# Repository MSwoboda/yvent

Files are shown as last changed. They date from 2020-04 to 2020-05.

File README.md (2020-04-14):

# yVent
 
***Disclaimer:** yVent is not a medical device. yVent must not replace FDA/CE-mark ventilation support. yVent is an experimental device which should only be considered in emergency scenarios as an alternative to death due to equipment shortage.*

## Summary

yVent is a pressure-triggered, 3D printable, emergency ventilator. The device has no moving parts and consits of 2 pieces of plastic. It is designed around an aerodynamic behavior known as the Coandă effect (It is a bistable fluidic amplifier). The device produces cyclical pressure changes, which can support patient breathing, while allowing for patient actuation and eliminating the possibility of dissynchrony. The device was designed and developed as a last resort ventilator for major clinical centers in Philadelphia.

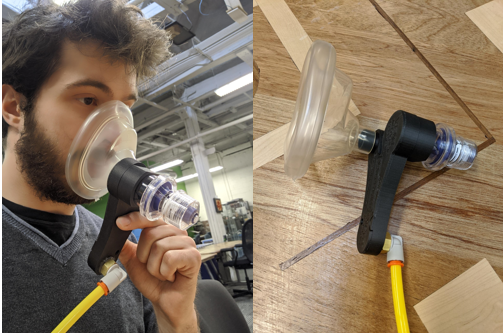
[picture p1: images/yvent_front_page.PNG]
YVENT yVent Inside


### Features
- Adjustable PIP pressure of 0-50 [cmH2O] 
- PEEP (0-20[cmH2O]) (w/ PEEP valve)
- Operating supply 20-140 [cmH2O] pressure source (air regulator or blower)  
- Can be actuated with patient breathing (no risk of asynchrony)
- Regulated inhale/exhale phase (I/E time, I/E ratio can be adjusted by modifying circuit compliance, resistance or by adding a controlled air leak)

### Risks

The device is a simple pneumatic oscillator triggered by pressure meant to sustain or support breathing. It pumps air in to a set pressure threshold, reverses flow, pumps air out to a set pressure threshold and resets. It cannot deliver a set volume of air (without an additional components), trigger alarms, display measurements, clear mucus, or perform many other critical functions of modern-day ventilators. 

### Failure Modes

yVent is reliable if the following requirements are satisfied:
1) Dimensional accuracy of the inlet and channel wedge is maintained
2) Seal of all chambers of the device is maintained
3) Air flow through the device is greater than leaks in patient circuit

yVent can fail in the following way:
- Violation of requirement 1 will change the pressure thresholds and pneumatic behavior of the circuit.
- Violation of requirement 1 may result in high frequency oscillation
- Violation of requirement 2 & 3 will result in no actuation 

## Theory of Operation

When pressure is applied to the input terminal of the yVent, the air flow stream created by the narrowing in the geometry creates a vortex (Coanda effect) which attaches the stream to the patient output channel. When the flow stream encounters resistance on the output terminal (increased pressure in patient's lungs), the first vortex collapses and the air flow stream redirects to the second output channel (again creating the Coanda effect vortex). In this fludic configuration, air flows from the patient output channel to the output terminal in addition to from the input terminal to the second terminal. This allows for exhale of gas. Once pressure in the patient's lungs reaches the threshold pressure, the second vortex collapses and restarts the cycle. Our design uses a different approach to create the Coanda vortex effect but functionally they are the same. 

## Testing and Validation

### Testing Setup
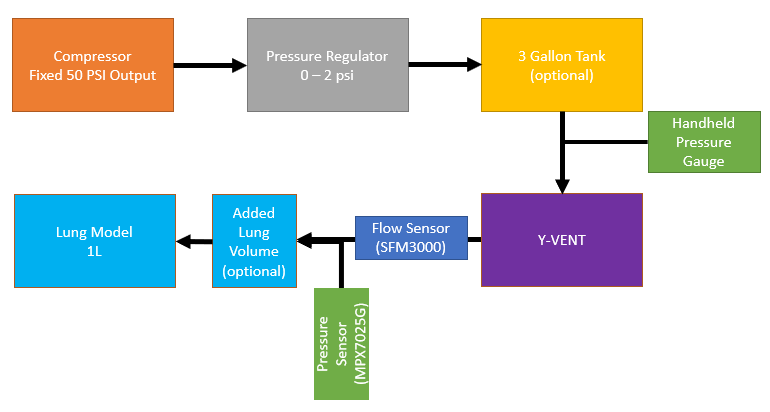
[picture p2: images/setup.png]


The testing setup aims to replicate a hospital air pressure supply of ~50 psi output connected to a 0-2 psi regulator. The pressure supply is connected to a 3 gallon tank to equalize pressure changes and flow. This is useful for testing and prototyping but not necessary for end-device as long as 2 psi regulator can provide sufficient flow to the yVent. The regulator pressure is monitored with a handheld pressure gauge.

The yVent connects to the output of the 2psi regulator and a lung simulator (MAQUET Test Lung 190 1L). The second output terminal (non-patient output) connects to a PEEP valve. The flow into the lung and pressure in the lung are monitored and recorded. The following data has been collected using this setup for two version of the yVent. Software of the measurement station can be found in the Measurement folder. Figures presented summarize the behavior of the yVent for different input pressures ranging from 40cmH2O to 120 cmH2O. If no measurement is present for a a given input pressure, it can be assumed that the device cannot work under these conditions (ex. peak inhale pressure of 20 cmH2o and 20 cmH2o PEEP causes oscillations).

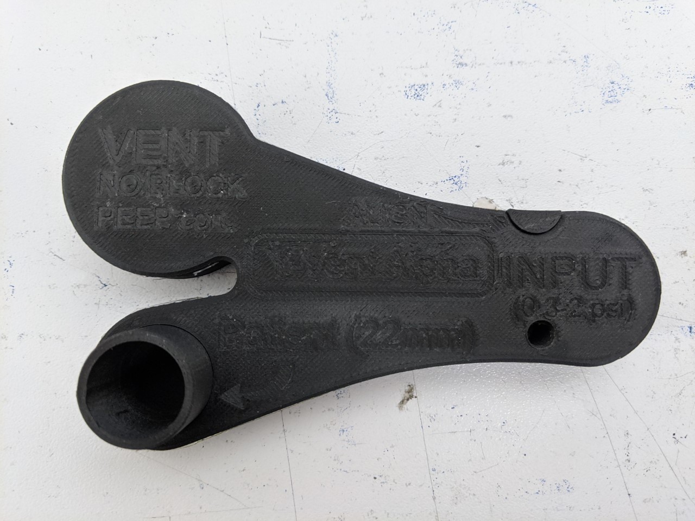
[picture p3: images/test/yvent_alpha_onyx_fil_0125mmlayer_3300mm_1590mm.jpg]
YVENT yVent Inside


### Results - Markforged 3D Printed Version [Onyx No Fiber Filament | 0.125mm layer]

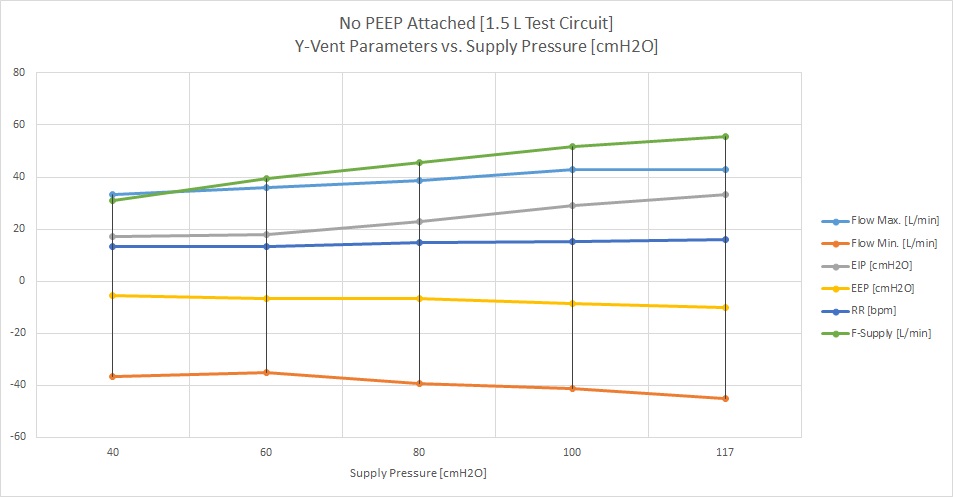
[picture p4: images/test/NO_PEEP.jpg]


Figure 1: No PEEP. 

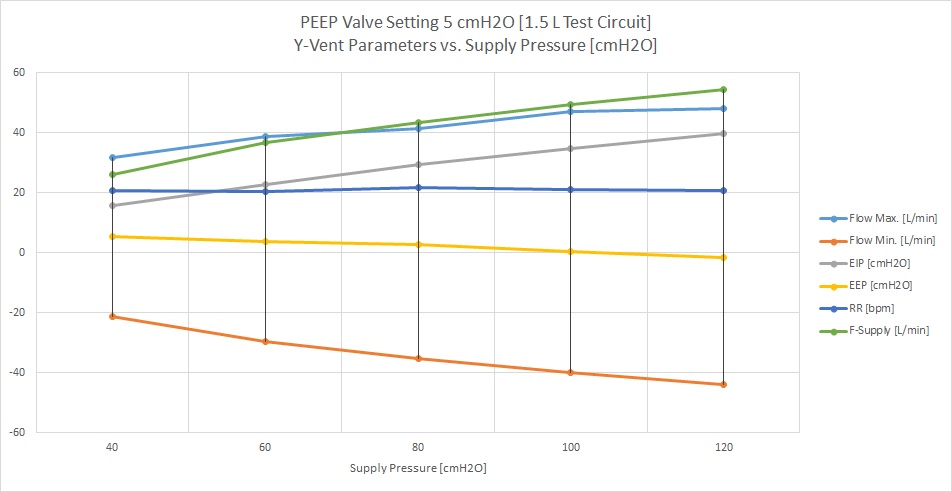
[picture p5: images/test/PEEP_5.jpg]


Figure 2: 5 cmH2O PEEP. 

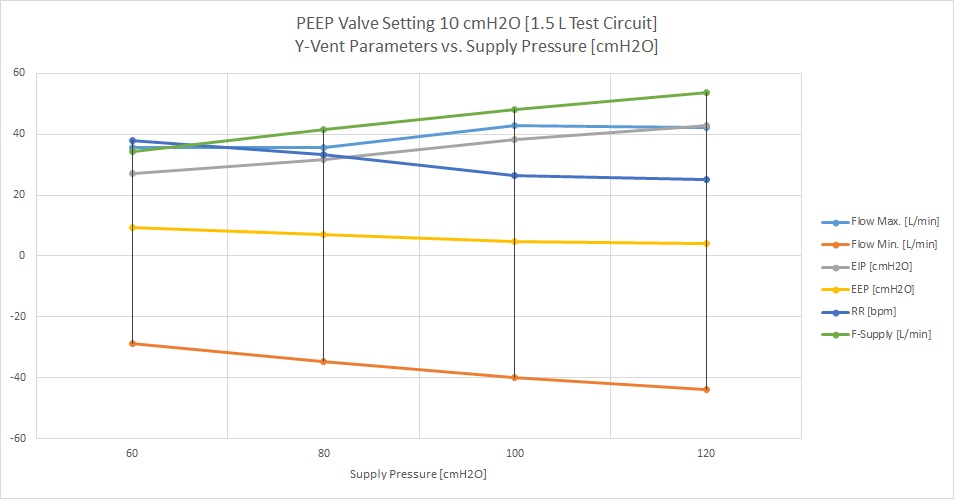
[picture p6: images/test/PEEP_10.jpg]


Figure 3: 10 cmH2O PEEP. 

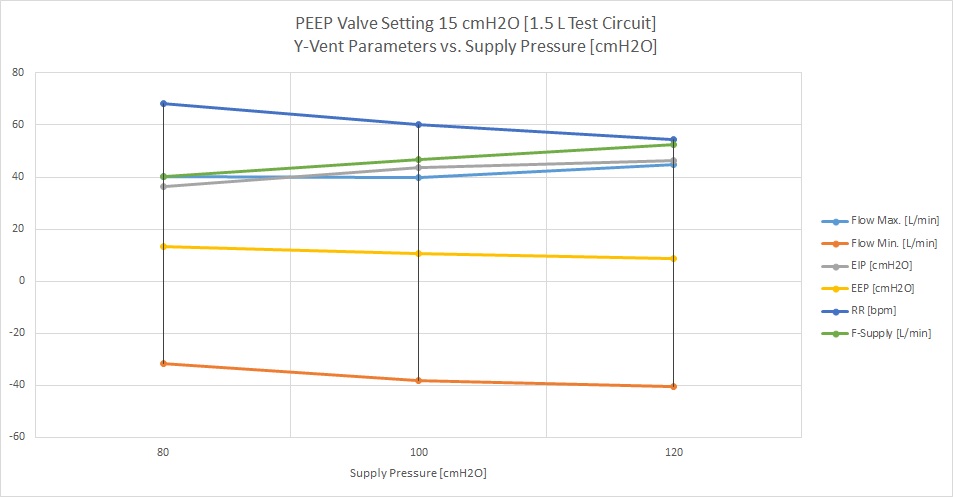
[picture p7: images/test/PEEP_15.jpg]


Figure 4: 15 cmH2O PEEP. 

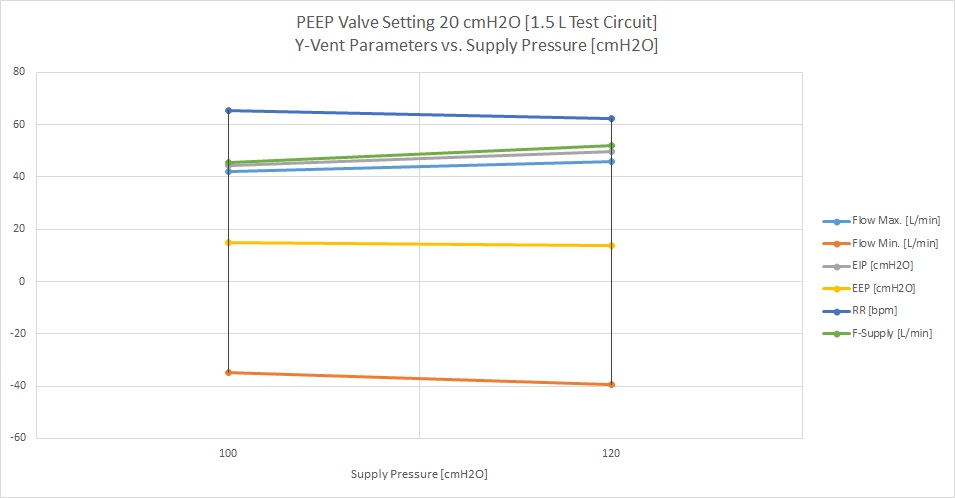
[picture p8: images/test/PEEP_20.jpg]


Figure 5: 20 cmH2O PEEP. 

### Results - Prusa MK3 [Hatchbox PLA Gray | 0.200mm layer | 0.2 SPEED MK3 Prusa Slicer Profile]

yVent printed in PLA shows similar behavior to the Onyx version. However, we believe there may be more variability between prints. We will post results when we test and validate several PLA devices. (Video of test: https://www.youtube.com/watch?v=HLaus3BIPC4)

YVENT yVent Inside

## Components and Modules

### Main Body
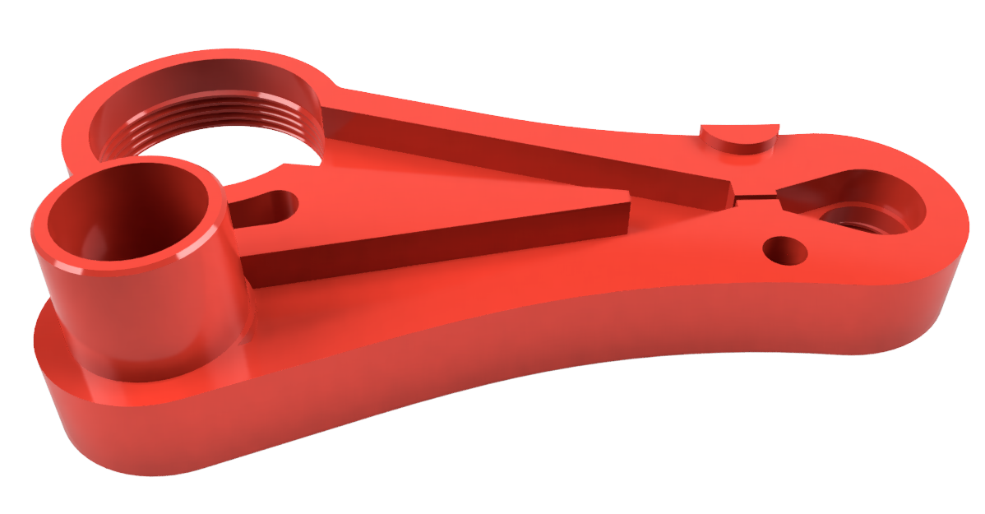
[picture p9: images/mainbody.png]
BODY yVent Inside

The main functional component of yVent. Consists of main input port for 0.3-2 psi regulated pressure, standard 22mm patient output port, and threaded vent port. The threaded port mates with the PEEP adapter to provide a stanard PEEP recepticle. The threaded port can also be used with a one-way HEPA filter to reduce aeorosolization of viral and bacterial particles. 

### Cover Plate
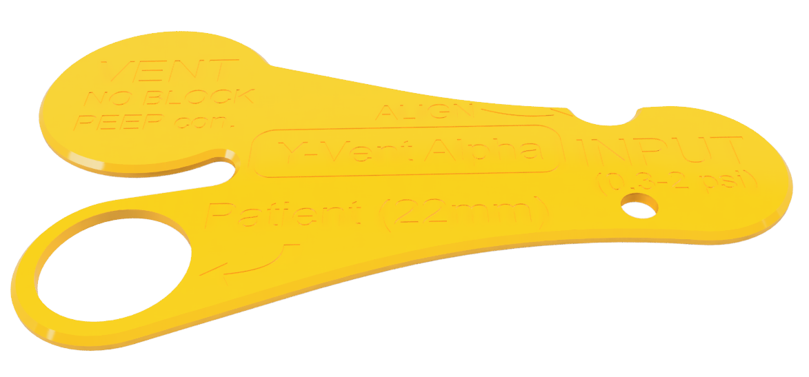
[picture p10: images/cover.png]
COVER yVent Inside

Cover plate is used to seal all channels and provide basic use information of the device. 

**Note:** Special care needs to be taken to glue the cover plate to the main body. This is the most common point of failure during assembly.

### PEEP Adapter
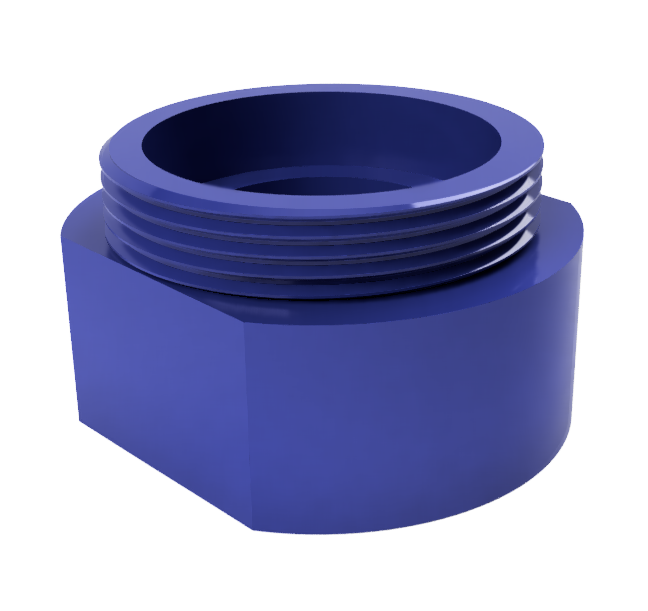
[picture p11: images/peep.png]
PEEP ADAPTER yVent Inside


PEEP adapter theads into the main body vent and provides one 22mm and one 33mm port for stanard PEEP valves. The connector can also connect to a HEPA flter.

## Manufacturing & Assembly

Assembly Video: https://www.youtube.com/watch?v=hZ9rezzCuwM  

### Explanation
yVent has been designed to be enitrely 3D printed. However, CAD and STL file folders include both 3D printable versions and a rough version adapted for CNC milling and injection molding (threads removed, holes sized for tapping, overhangs removed).

The design has been printed and tested using Markforged Onyx One and Prusa i3 Mk3 printers (see testing sections).

### Medical Grade Silicone Adhesive Method [preferred]

This method creates a robust seal between the main body and cover using a medical grade silicone rubber. This is the preferred method of sealing the part.

#### Tools
- Spatula
- Q-Tip
- Medical-grade Silicone Adhesive 
- Paper towel

#### Instructions

1) Remove supports from 3D printed parts and prepare tools. 

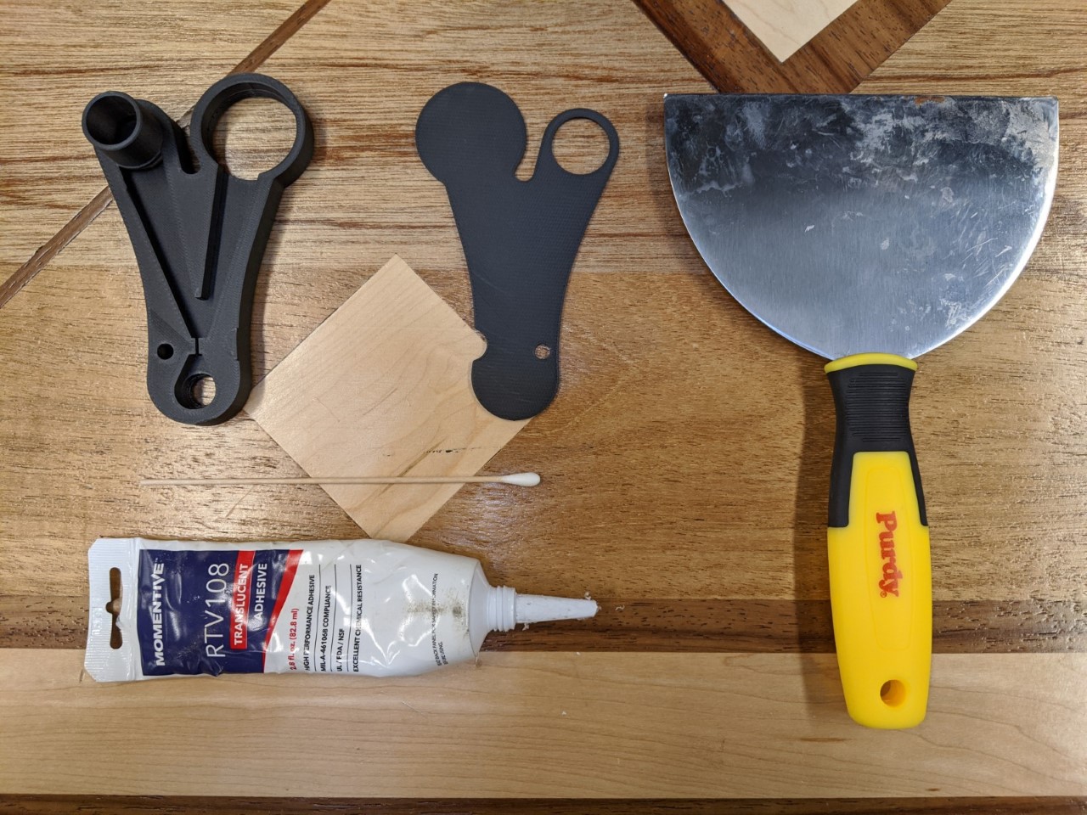
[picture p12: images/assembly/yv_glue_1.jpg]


2) Add blob of adhesive to the smooth side of cover (side without writing). The amout of adhesive should be enough to create a thin (0.2-1mm) layer.

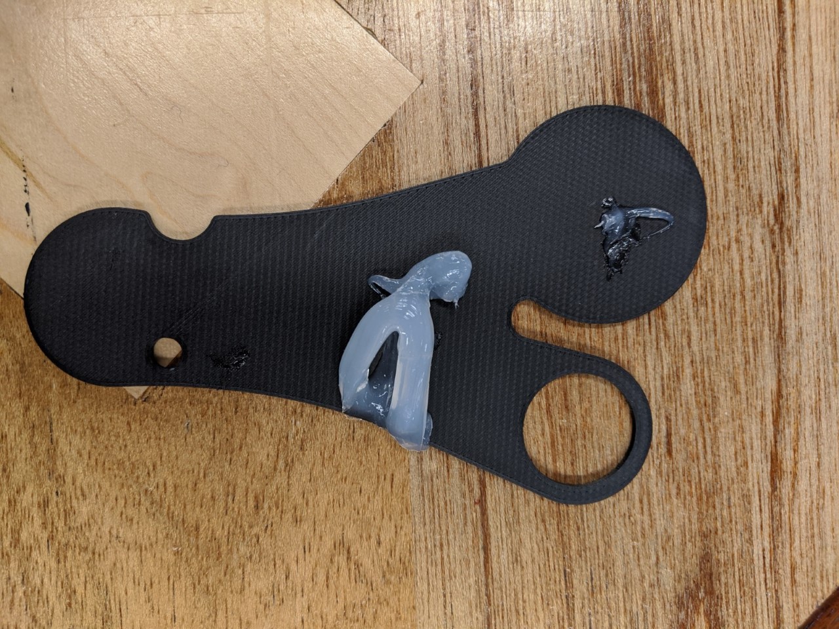
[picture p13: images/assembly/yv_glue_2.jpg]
Step2 yVent Inside


3) Distribute adhesive evenly with spatula. This should create a uniform layer with no pits. Fill any gaps with more adhesive and smooth out with spatula.

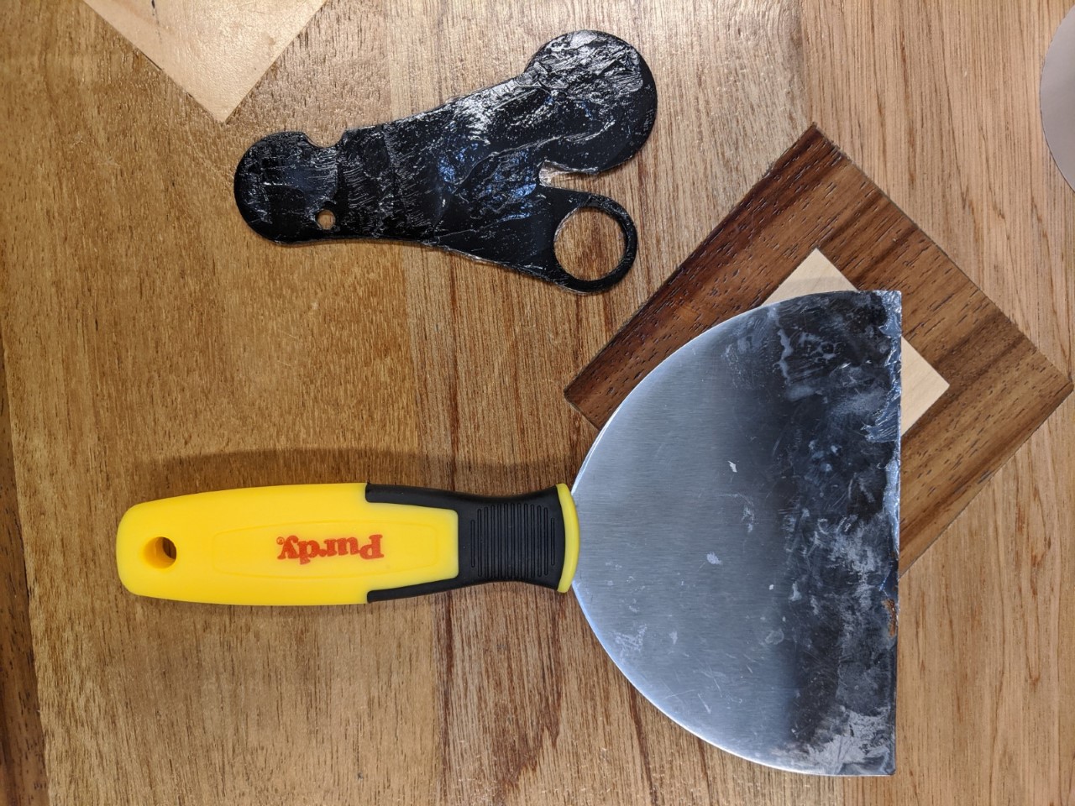
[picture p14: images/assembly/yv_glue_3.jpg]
Step3 yVent Inside


4) Lock the cover on output port and align with protrusion on the main body.

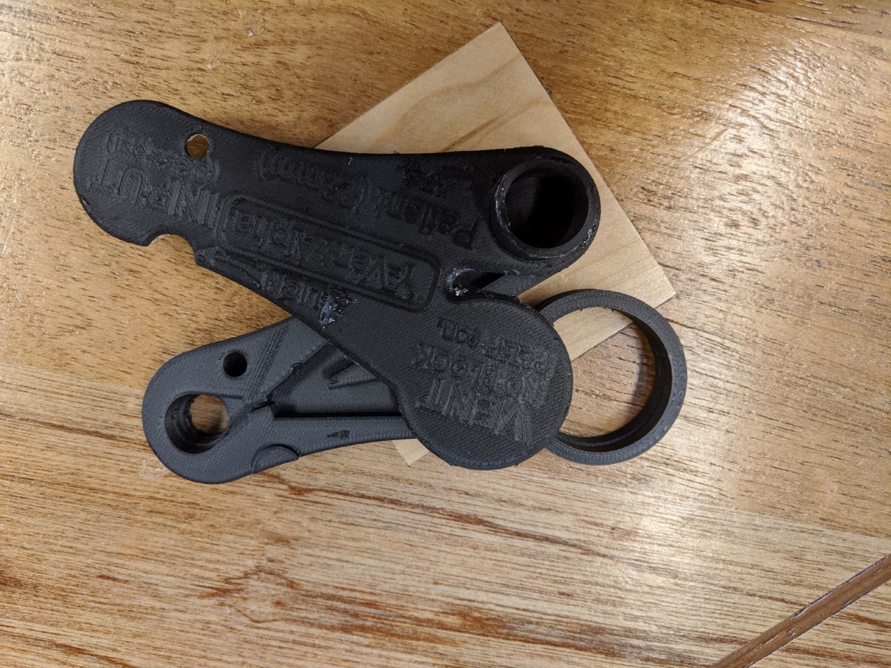
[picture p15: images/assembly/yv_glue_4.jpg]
Step4 yVent Inside


5) Clean any adhesive leaking out with a paper towel.

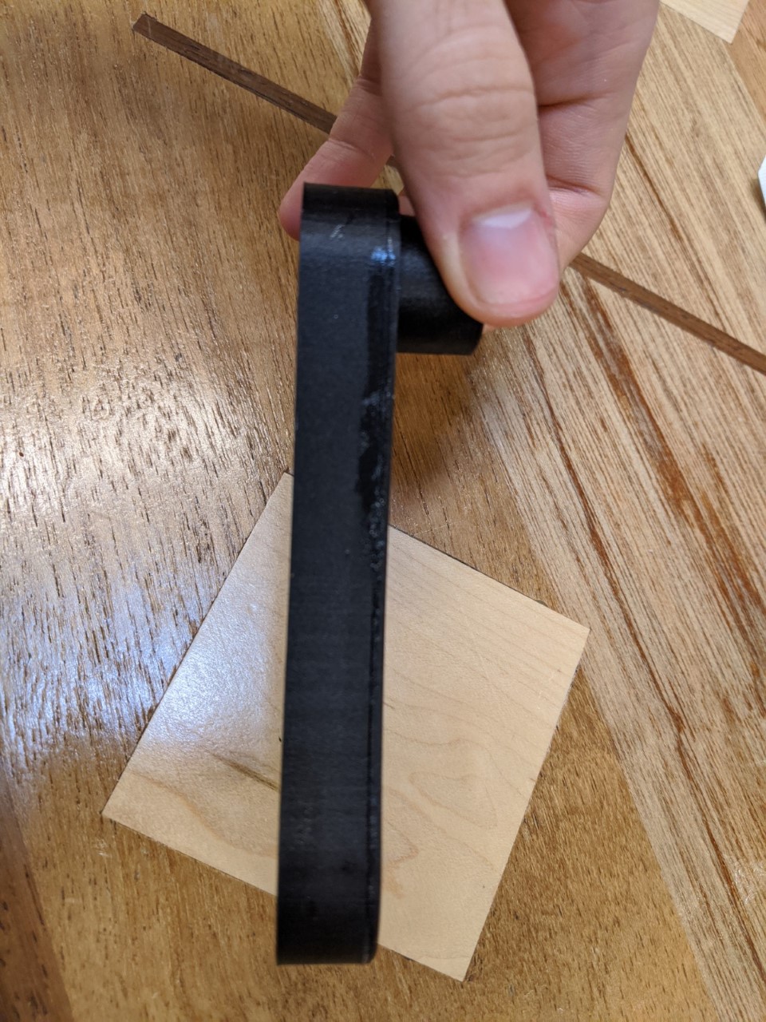
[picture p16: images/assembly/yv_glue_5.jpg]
Step5 yVent Inside


6) Apply pressure to the part and leave to try until adhesive is set. Time and pressure will depend on adhesive type. Note the setting and curing time.

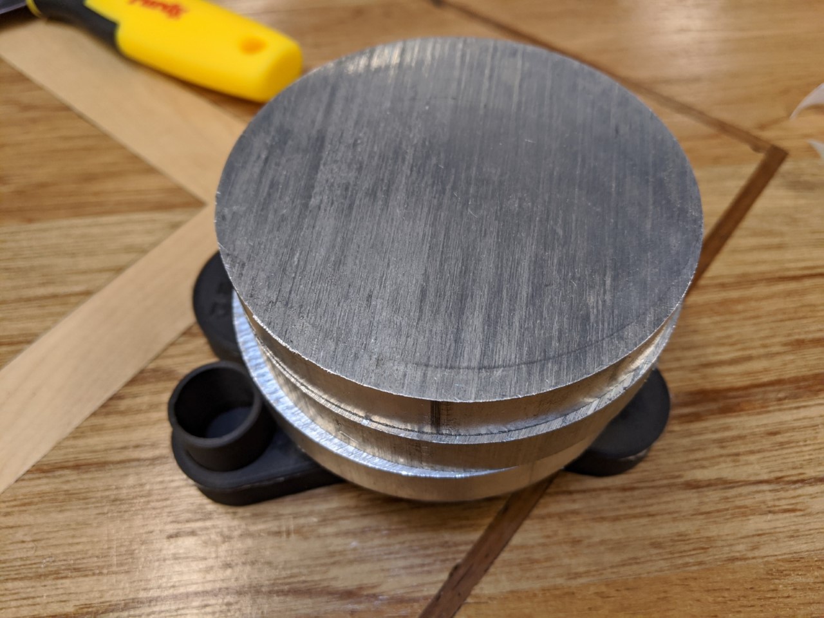
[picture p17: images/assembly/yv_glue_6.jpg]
Step6 yVent Inside


### Double Sided Tape [prototyping]

#### Tools
- Scissors
- Scalpel or sharp knife
- Strong Double-Sided Tape
- Hot air gun (optional)

#### Instructions

1) Apply a single strip of double-sided tape to cover the input port and one arm of the yVent. A single strip should cover the input port, narrowing at the input port, and wedge dividing the yVent into two channels.

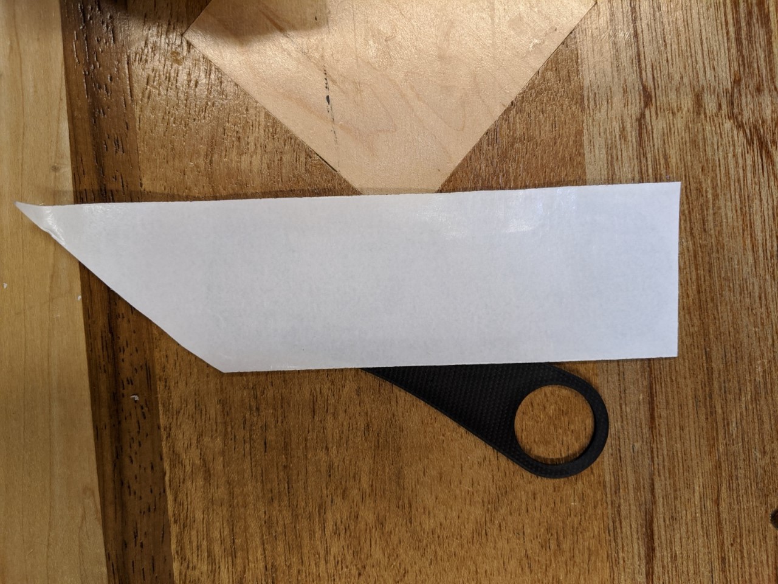
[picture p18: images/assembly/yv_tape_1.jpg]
 

2) Apply second strip to the remaining part of the cover. The two strips should create a small (less than 0.5 mm overlap) to provide optimal sealing.

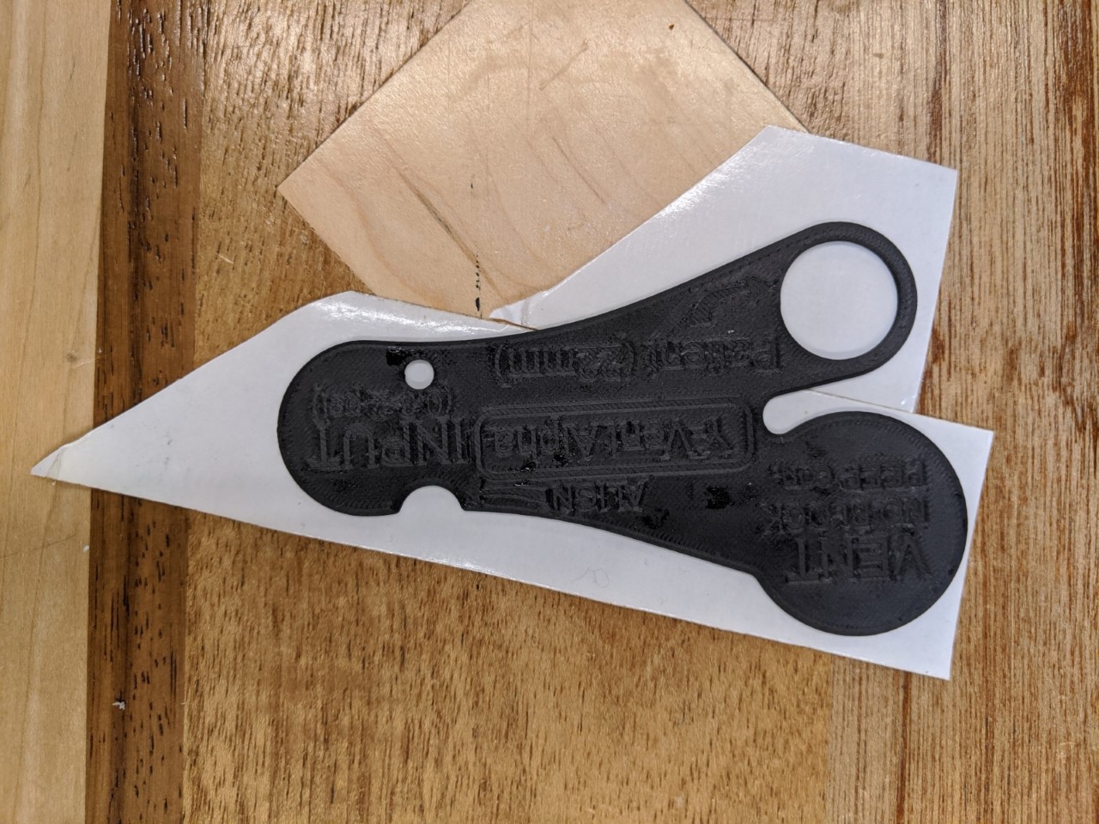
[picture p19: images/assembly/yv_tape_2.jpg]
 

3) Cut the tape with a scalpel or scissors to align with the edge of the cover.

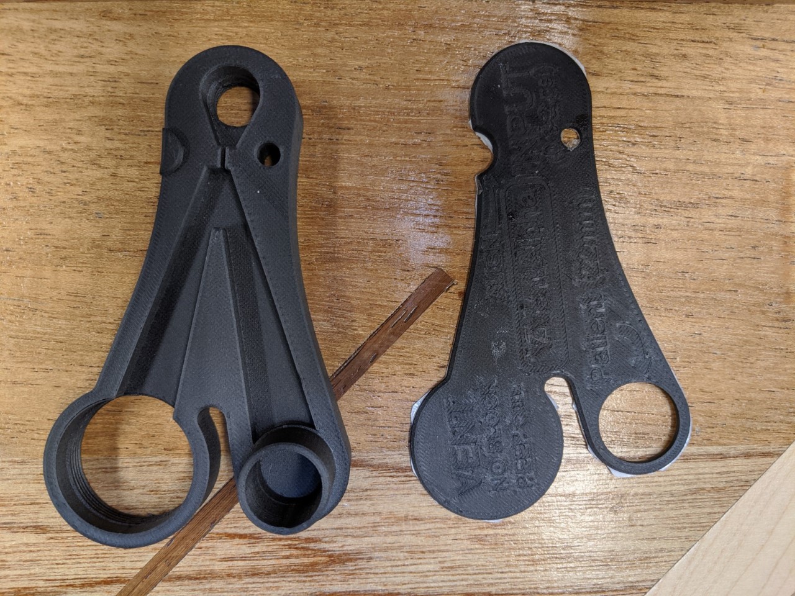
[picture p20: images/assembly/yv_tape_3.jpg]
 

4) Lock the cover on the output port and align with protrusion on the main body. Remove any protruding tape with a scalpel. The protruding tape can also be removed with a hot air gun (**Note:** Apply a small amount of heat to only melt the tape and not the plastic of the yVent).

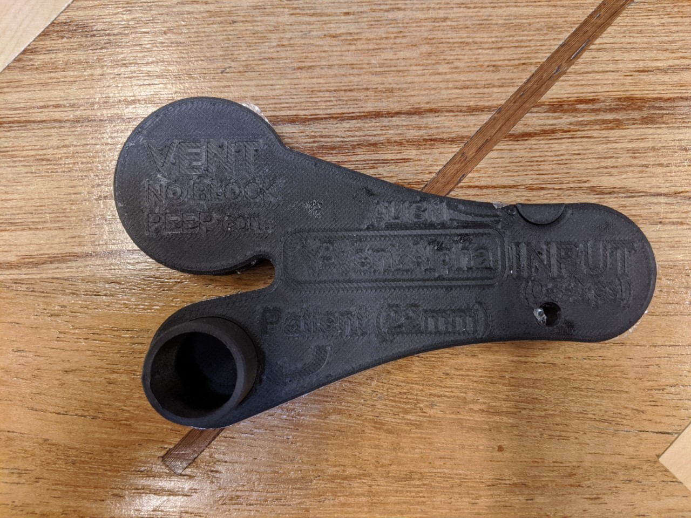
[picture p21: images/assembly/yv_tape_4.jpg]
 

5) Apply pressure to the part.

 Step1 yVent Inside

### Input Port Mount

The yVent has a standard 1/4 NPT thread on the input port, which can fit a wide variety of connectors (like push to connect, barb). Select the connector most appropriate for your environment (testing, clinical). When inserting the connector apply a small amount of glue to the threads to seal it. 

**Note:** Make sure the connector's edge does not protrude over the floor of the yVent channels. 

**Note:** Make sure that any adhesive applied to the threads does not leak into the input chamber, especially the narrowing after the input port.

## Failure Reporting

We encourage everyone interested in the project to 3D print and try out the yVent on your own. All you need is a 3D printer, lung model (could be a balloon but ventilator test lungs works best), and a 0.3-2psi pressure source. If you'd like to add PEEP, a PEEP valve is necessary. Please post all problems you enocunter in the Github's issues section along with a description of how the device was printed, the test setup, a detailed description of the problem, and possible solutions.

## Literature

[1] [The Fluid Amplifier and its Application in Medical Devices](https://github.com/MSwoboda/yvent/blob/master/literature/The_Fluid_Amplifier_and_its_Application_in_Medical.pdf)

[2] [Taxonomic Trees of Fluidic Oscillators 
](https://www.epj-conferences.org/articles/epjconf/pdf/2017/12/epjconf_efm2017_02128.pdf)

[3] [Experimental Comparison between the Flow Field of Two Common Fluidic Oscillator Designs](https://www.researchgate.net/publication/271645509_Experimental_Comparison_between_the_Flow_Field_of_Two_Common_Fluidic_Oscillator_Designs)

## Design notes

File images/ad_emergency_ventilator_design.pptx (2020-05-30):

## AIR-AD: EVS Concept Notes

## Rapidly manufactured ventilator system specification:

https://www.gov.uk/government/publications/coronavirus-covid-19-ventilator-supply-specification/rapidly-manufactured-ventilator-system-specification

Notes: ICU min req specs:

1) volume control: you can set the tidal volume for each breath
2) set the respiratory rate
3 be able to set the PEEP, or at least a constant PEEP that is chosen by manufacturing team


Preferably able to do these:
A) set inspiratory flow
B) measure PIP (peak inspiratory pressure)

## Design Inputs Summary - Ventilation

General
- Mode: volume or pressure control mode (Volume preferred)
- Volume control: 250ml – 500ml (+/- 50ml) in at least 2 increments (ex 350 ml and 450 ml)
- Breathing Rate: 10-40 Breaths per minute
- Inspiratory/Expiratory (I:E) ratio fixed at 2 or adjustable 1.0 to 3.
- Set PEEP: 5-20 cmH2O or one fixed (setting accuracy of PEEP (+/- 10%))
- Maximum PIP 40-50 cmH2O
Optional:
- Measure PIP (peak inspiratory pressure) 50 cmH2O
- Flow, pressure, and volume waveforms

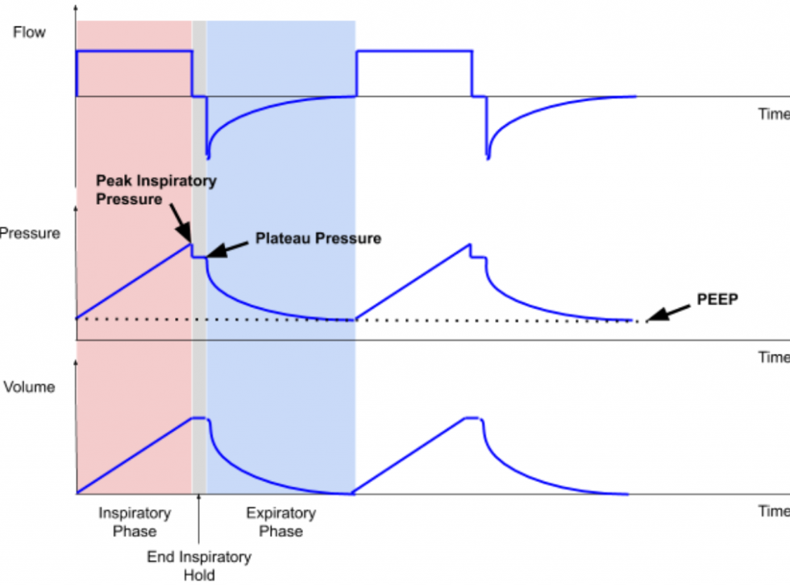
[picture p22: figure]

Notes: ICU min req specs:

1) volume control: you can set the tidal volume for each breath
2) set the respiratory rate
3 be able to set the PEEP, or at least a constant PEEP that is chosen by manufacturing team


Preferably able to do these:
A) set inspiratory flow
B) measure PIP (peak inspiratory pressure)

## Design Inputs Summary - Operation

- The devices is valuable if it can reliably provide the clinical function, while not introducing substantial risk
- Must interface with standard pneumatic connectors
- Can’t interfere or damage other equipment
- Must operate reliably 24 hours a day for at least 14 days.
- Must be intuitive to use for medically trained professional

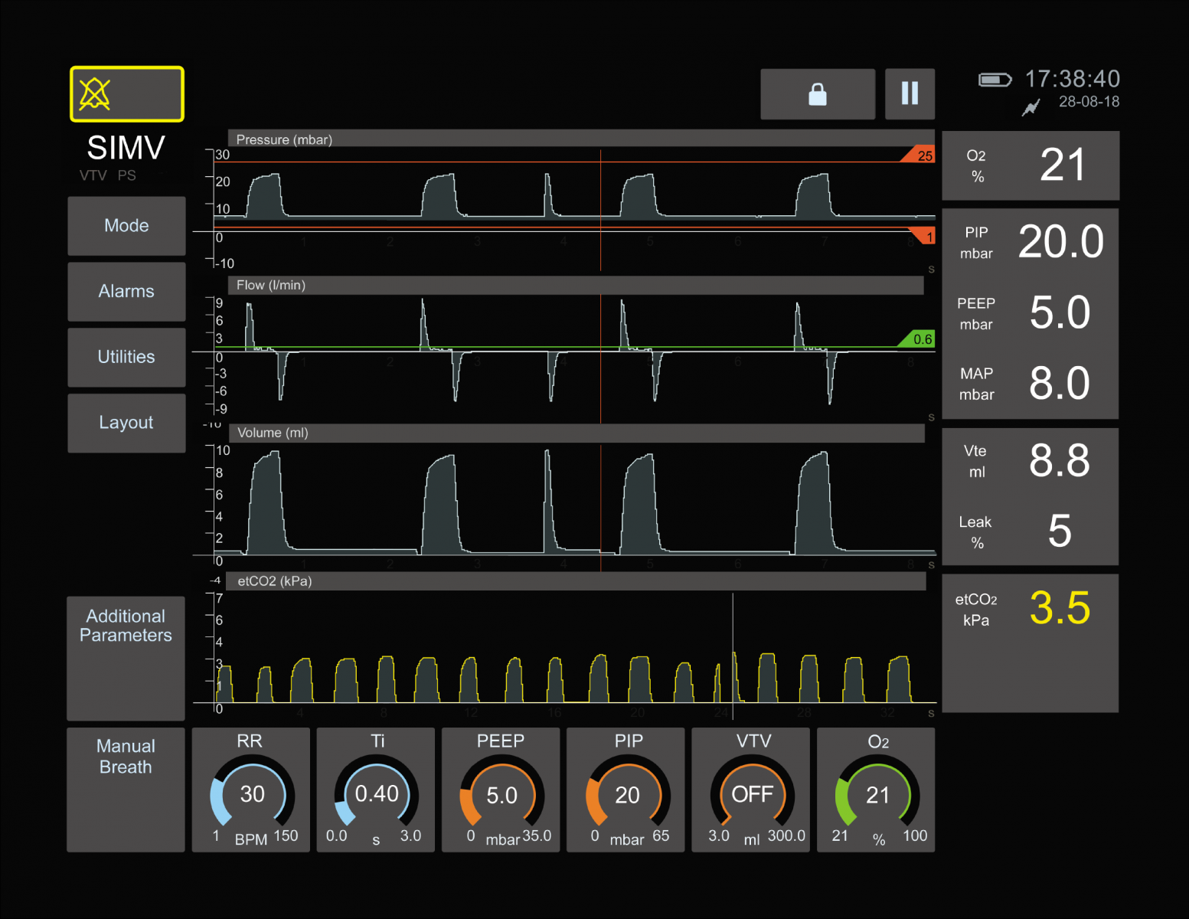
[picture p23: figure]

## Design Inputs Summary – Part Availability

- Part or direct substitute must be available in quantities of 120
- Device should use standard, industrial, certified components whenever possible
- Device should be built using a modular architecture allowing for swapping of components based on availability

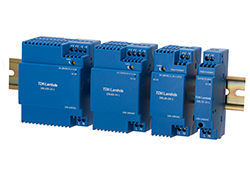
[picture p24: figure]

## Power Subsystem

(Optional)

OFF SWITCH

SSR Latch

CONTROLLER

AC PLUG

OUTSIDE

DEVICE

ON/OFF
SWITCH

AC to 24 VDC

ACTUATOR DRIVER

(Keep External)

BATTERY

24V UPS

## Pneumatic Subsystem

O2 Mixer

Air Input

Emergency Air Input

Pressure Port Barb

22mm Air Port

OUTSIDE

DEVICE

Anti asphyxiation Valve

Overpressure Valve 40 cmH2O

ACTUATOR
(electrically powered)

Ambubag/Cylinder
Pump

One-way Valve

Overpressure Valve 60 cmH2O
(optional)

## External Air Circuit

PEEP Valve

Mask/Tube

Patient Tubing

O2 Mixer
(find is available)

O2 Cylinder

Pressure Port Barb

22mm Air Port

OUTSIDE

DEVICE

## Control Subsystem:

Position Feedback
Sensor

DEVICE

Output Flow Sensor

Controller
(PLC unitronix)

Actuator Driver

Breathing Rate Pot. (#2)

Actuator

Endstop

Ambubag/Cylinder
Pump

Patient Pressure Sensor

GUI Screen
(optional)

Auxiliary Pressure Sensor

Tidal Vol Pot. (#1)

I/E Potentiometer (#3)

On-Demand Inhale Button
(optional)

## User Interface Concept

Air and Pressure Port

Inlet Port & Emergency Inlet

Programmable LCD Display

Critical User Interface

AC Cord Wrap Handles

Handle

AC IN

Push On

Power Switch

Tidal

Rate

I/E

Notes: ICU min req specs:

1) volume control: you can set the tidal volume for each breath
2) set the respiratory rate
3 be able to set the PEEP, or at least a constant PEEP that is chosen by manufacturing team


Preferably able to do these:
A) set inspiratory flow
B) measure PIP (peak inspiratory pressure)

## Piston Actuator Concept #1

Linear Actuator

Stroke 3-5”

Stroke vs max reps vs freq
Flow rates can be linear
Physical limit switches
Some linear actuators have encoder
Plate sitting on 4 shafts with bearings
Complexity:
How to lead the actuator
Tolerance between the cylinder
Can be adressed with shafts

Plate

Bellows

Check Valve #1

Check Valve #2

Cylinder

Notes: ICU min req specs:

1) volume control: you can set the tidal volume for each breath
2) set the respiratory rate
3 be able to set the PEEP, or at least a constant PEEP that is chosen by manufacturing team


Preferably able to do these:
A) set inspiratory flow
B) measure PIP (peak inspiratory pressure)

## Piston Actuator Concept #2

Linear Actuator

Stroke 3-5”

Floating O-Ring

Plate

Look into piston pumps
Existing components
Like cylinders

Check Valve #1

Check Valve #2

Cylinder

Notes: ICU min req specs:

1) volume control: you can set the tidal volume for each breath
2) set the respiratory rate
3 be able to set the PEEP, or at least a constant PEEP that is chosen by manufacturing team


Preferably able to do these:
A) set inspiratory flow
B) measure PIP (peak inspiratory pressure)

## Piston Actuator Concept #3

Plate

Stroke 3-5”

Bellows

Linear Actuator

Check Valve #1

Check Valve #2

Cylinder

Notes: ICU min req specs:

1) volume control: you can set the tidal volume for each breath
2) set the respiratory rate
3 be able to set the PEEP, or at least a constant PEEP that is chosen by manufacturing team


Preferably able to do these:
A) set inspiratory flow
B) measure PIP (peak inspiratory pressure)

## Piston Actuator Concept #4

Cylinder

O-Ring

Check Valve #1

Plate

Check Valve #2

Scissor type linkage

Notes: ICU min req specs:

1) volume control: you can set the tidal volume for each breath
2) set the respiratory rate
3 be able to set the PEEP, or at least a constant PEEP that is chosen by manufacturing team


Preferably able to do these:
A) set inspiratory flow
B) measure PIP (peak inspiratory pressure)

## Penn ICU Design Inputs :

Main:
- Volume control – set tidal volume breathing
- Set respiratory rate
- PEEP set
Optional:
- Set inspiratory flow
- Measure PIP (peak inspiratory pressure)

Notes: ICU min req specs:

1) volume control: you can set the tidal volume for each breath
2) set the respiratory rate
3 be able to set the PEEP, or at least a constant PEEP that is chosen by manufacturing team


Preferably able to do these:
A) set inspiratory flow
B) measure PIP (peak inspiratory pressure)

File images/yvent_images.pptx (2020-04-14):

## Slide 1

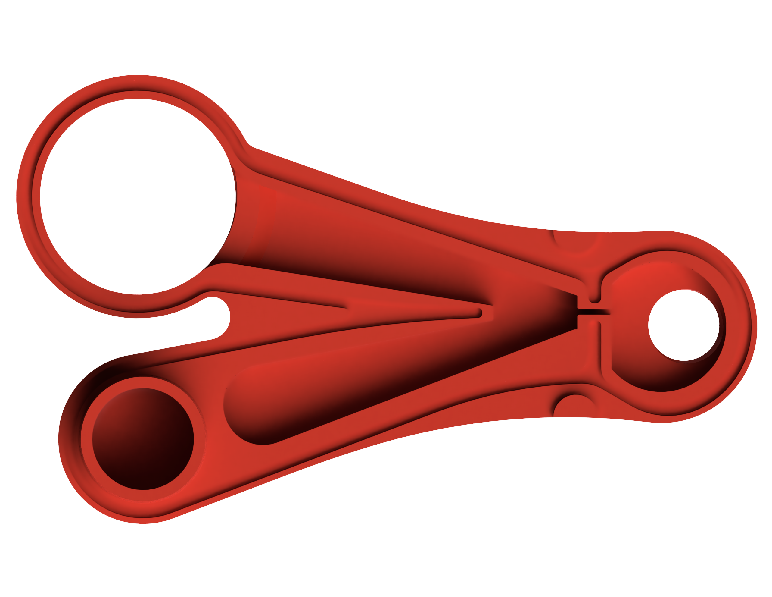
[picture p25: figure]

Vent

Diffuser

Diffuser

Input

Patient Port

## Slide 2

Compressor
Fixed 50 PSI Output

Pressure Regulator
0 – 2 psi

3 Gallon Tank
(optional)

Handheld Pressure Gauge

Lung Model
1L

Added Lung Volume (optional)

Y-VENT

Flow Sensor (SFM3000)

Pressure Sensor (MPX7025G)

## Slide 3

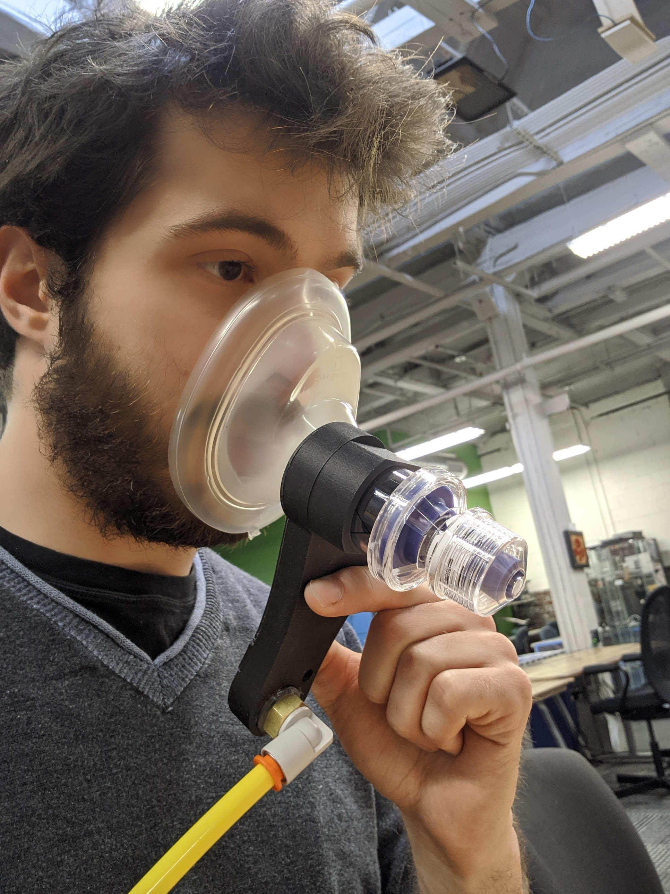
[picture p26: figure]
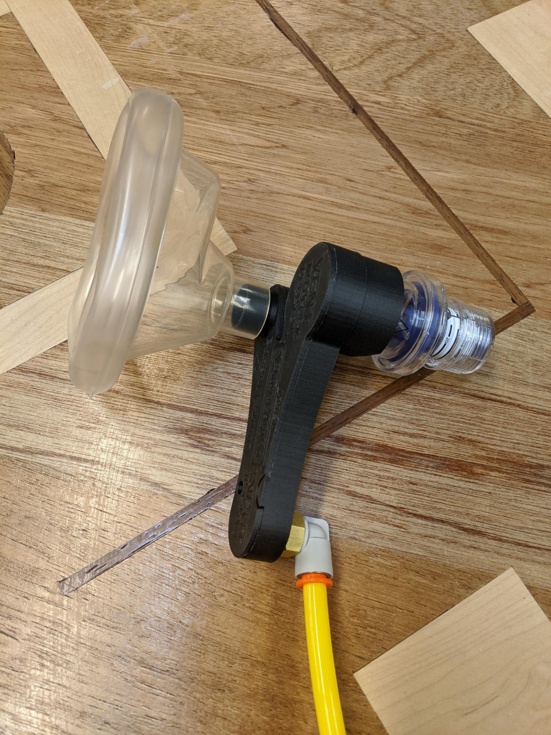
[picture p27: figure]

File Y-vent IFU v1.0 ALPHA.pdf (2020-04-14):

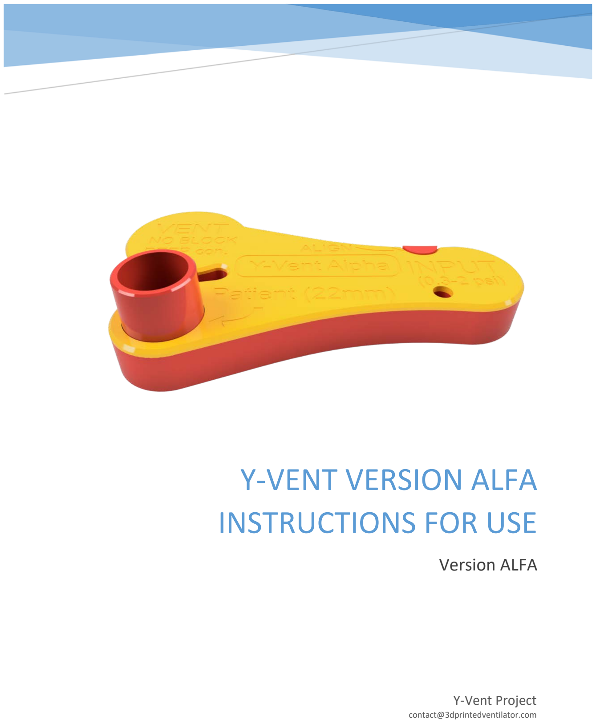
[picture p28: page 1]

# Y-VENT VERSION ALFA INSTRUCTIONS FOR USE

### Version ALFA

Y-Vent Project
contact@3dprintedventilator.com

1
Y

-VENT INSTRUCTIONS FOR USE V1.0 04

-07

-2020 ALFA

2
Y-VENT INSTRUCTIONS FOR USE V1.0 04-07-2020 ALFA

### Table of Contents

3

## 1.Introduction

The Y-vent is not a medical device. It cannot be used as such. Please refer to your local jurisdiction to learn a legal frame work for the emergency usage. The unit can be used in two basic configurations: 1) NO PEEP 2) PEEP. It provides physiological pressures if a proper pressure source is connected to the input port AND a compliant volume is connected to the patient port. The patient pressure can be adjusted by adjusting the supply pressure and the PEEP valve if used in PEEP configuration.

### Risks

The device is a simple pneumatic oscillator triggered by pressure. It pumps air in to a set pressure threshold, reverses flow, pumps air out to a set pressure threshold and resets. It cannot: deliver a set volume of air, trigger alarms, display measurements, clear mucus, or perform many other critical functions of modern-day ventilators.

### Basic Failure Modes

Y-Vent is reliable if the following requirements are satisfied:
1. Dimensional accuracy of the inlet and channel wedge is maintained
2. Seal of all chambers of the device is maintained
3. Air flow through the device is greater than leaks in patient circuit (preferably no leaks)
Y-Vent can fail in the following way:
- Violation of requirement 1 will change the pressure thresholds and pneumatic behavior of the circuit.
- Violation of requirement 1 may result in high frequency oscillation
- Violation of requirement 2 & 3 will result in no actuation

### Theory of Operation

When pressure is applied to the input terminal of the Y-Vent, the air flow stream created by the narrowing in the geometry creates a vortex (Coanda effect) which attaches the stream to the patient output channel. When the flow stream encounters resistance on the output terminal (increased pressure in patient's lungs), the first vortex collapses and the

4

air flow stream redirects to the second output channel (again creating the Coanda effect vortex). In this fluidic configuration, air flows from the patient output channel to the output terminal in addition to from the input terminal to the second terminal. This allows for exhale of gas. Once pressure in the patient's lungs reaches the threshold pressure, the second vortex collapses and restarts the cycle. Our design uses a different approach to create the Coanda vortex effect, but functionally they are the same.

5

## 2.Y-vent basic features

### Fully 3D-printed

Main Body

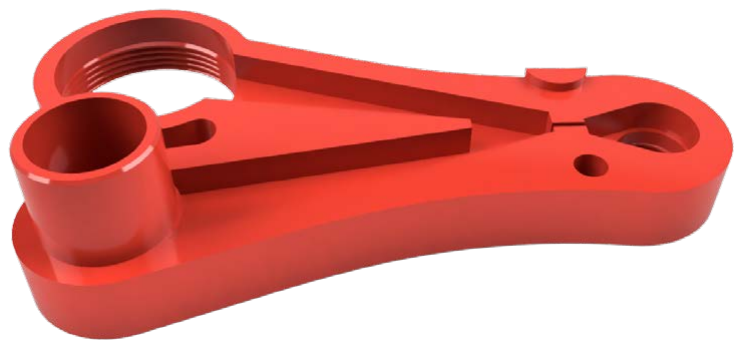
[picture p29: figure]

Figure 1. 3D printable main body
The main functional component of the Y-Vent consists of main input port for 0.3-2 psi regulated pressure, standard 22mm patient output port, and threaded PEEP/vent port. The threaded port mates with the PEEP module to provide a standard PEEP receptacle. The threaded port can also be used with a one way HEPA filter to reduce aeorosolization of viral and bacterial particles.

6

Cover Plate

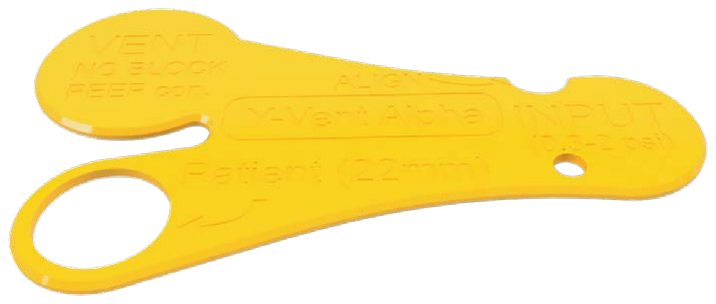
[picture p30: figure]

Figure 2. 3D printable cover plate
Cover plate is used to seal all channels and provide basic use information of the device. Note: Special care needs to be taken to glue the cover plate to the main body. This is the most common point of failure during assembly.

PEEP Module

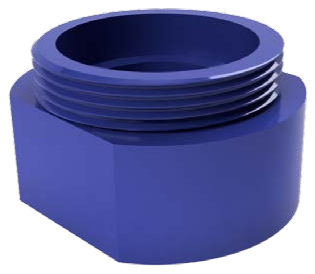
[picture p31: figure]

Figure 3. 3D printable PEEP Module
The Y-vent can be fully printed. The list of printers which are suitable for this job is attached (Attachment A – list of printers). The printed version has a full Pressure Support Mode, PEEP valve port, Fall back Respiratory Rate, and 3D printed PEEP valve can be printed as a separate module (released separately from the main ventilator). It will NOT have the Respiratory Rate adjustment module and oxygen module which

7

requires additional components and instructions (will be published separately). The Balloon for the RR module needs to be acquired separately.
Estimated printing time is 4 hours, but this may vary depending on the printer.

### No-moving-parts reliability

The Y-vent has no moving parts in the NO PEEP configuration, thus its reliability is limited only by the pressure source. As long as the pressure is supplied and a compliant volume connected to the output, the vent will cycle. Adding a PEEP valve will add moving parts (spring and membrane), thus the reliability may change.

### Assembly time: less than 10 minutes

The assembly can be done with a double sided tape, glue gun and an x-Acto knife. Equivalent glue and knife options are listed in Attachment B (Attachment B- tools needed). Respiratory Rate (RR) adjustment mode will require a balloon. Please see RR module assembly instructions (will be published separately).

### Cost - less than $12 (depends on the type of 3D printer)

The cost is basically the cost of the 3D printer filament, glue, and tape. Plus, the cost of the balloon (roughly an additional $10).

### Contamination limiting and Disposable

The Y-vent is a covid-19 specific device. It was designed to limit the contamination by being disposable and working always with positive pressure, so the contamination cannot cross beyond the vent to the pressure supply and modules connected on the pressure supply line. We do not recommend any disinfecting procedures as it wasn’t designed to withstand any disinfecting solutions or treatments. The unit should be safely disposed of after being disconnected from the patient and a new unit should be used. 3D printed units are not sterile!

### Basic mode – Pressure Support

The basic mode of operation is called Pressure Support. During the inhale phase, it will slowly reach the preset level (End Inspiratory Pressure), and then it will reverse the ventilation phase. Similarly, during the exhalation phase, it will reach the preset End Expiratory Pressure level and after that, it will reverse the ventilation phase to inhale. If the patient is breathing on his own, the vent will follow patient’s breathing pattern unless it falls beyond the Fall Back Respiratory Rate. If the patient doesn’t breathe, the

8

unit will breathe for him maintaining the preset respiratory rate (RR). Both pressures (End Expiratory and End Inspiratory) can be regulated by the supply pressure and the PEEP module. If the PEEP module is not installed, then the only adjustment available is the supply pressure level. The Y-vent can vary EIP between 5 and 50 cmH2O and the EEP between -5 and 0 or 5 and 20 cmH2O (in PEEP configuration). Pressures ranges may differ depending on the manufacturing quality, overall leakages, and stability of the pressure supply.

### PEEP (Positive End Expiratory Pressure)

The PEEP capability is provided by the PEEP module. The PEEP module is printed together with the main configuration and can be connected to a PEEP valve, which converts the unit to its PEEP configuration. Regular medical PEEP valves can be used, or a 3D printed version. Rotating the cap of the PEEP valve clockwise will increase the PEEP, and rotating it counterclockwise will decrease the PEEP. Refer to the markings on the PEEP valve to adjust it to the desired level. The 3D printed version has no markings and needs to be calibrated by the user. If the PEEP valve is 3D printed, then the opening pressures will change with the printer, filament, and slicer settings. ALWAYS CALIBRATE YOUR 3D PRINTED PEEP VALVE.

### Adjustable EIP and EIP

EIP and EEP will differ for the NO PEEP and PEEP configurations. Please refer to appropriate characteristics (Section 6).

### Adjustable RR

Because of the fact that the Y-vent will always try to achieve the preset pressures operating with relatively constant flow, the Respiratory Rate will depend on the volume and compliance of the breathing loop, including patient’s lungs.
If needed, the Respiratory Rate can be adjusted by connecting the Respiratory Rate module and a balloon. The balloon will slow down the respiratory rate to its minimum. If fine adjustment is desired, a volume limiting clamp can be used, please see the RR module manual.
When the PEEP valve malfunctions in the open position, the Y-Vent will start working in NO PEEP configuration. This will cause the pressure characteristics to change. Always check visually if the PEEP valve is working.
IF THE PEEP VALVE MALFUNCTIONS, THE PEEP WILL NOT BE MAINTAINED

9

### Supply pressure 60l/min(max) at 30 – 200 cmH2O

Pressure supply needs to provide medical grade air, please refer to your local procedures. This air will be pumped to the patient’s lungs. Make sure that the air has required quality. Tested regulators are listed in Attachment C.

### Connects to a trach tube or mask

The Y-vent works best with the Endotracheal tube (ETT), but can be also used with a mask. If the mask is used, it needs to be sealed off properly. Leaking mask may lead to suboptimal performance or even malfunction due to inability to reach the preset EIP or EEP. With unconscious patients, when the trachea is blocked, a mask may cause irregular cycles.

### Oxygen supply possible

Oxygen can be supplied via an oxygen module. FURTHER RECOMMENDATIONS WILL FOLLOW

10

## 3.Clinical considerations (Preliminary)

### Inspection before usage

After assembling the unit, a visual inspection should be performed. The unit can be roughly tested for leaks by blowing slightly positive pressure to the input port (e.g. 20 cmH2O), closing the patient and vent ports with fingers and listening to hissing sounds. If no leaks detected, the test lung (e.g. Maquet test lung 190 – with opened covers) should be connected to the patient port with a pressure transducer. Test the unit for min and max supply pressures in NO PEEP configuration. Refer to the Pressure tables to see if the values are comparable within 2cmH2O, if not, create your own tables using the Y-vent tables as a template. Connect a PEEP valve and test for 5, 10, 15, 20 cmH2O of PEEP, compare to Y-vent characteristics. If your results are within +/-2cmH2O, you can use Y-vent tables, if not, create your own tables using Y-vent tables as a template. Please note that not all PEEP values can be achieved with low input pressures. Refer to Y-vent characteristics. If no pressure transducer is available, a manometer can be used to observe EEP and EIP. If neither is available, a makeshift manometer can be produced from a transparent tubing filled with water (see video: https://www.youtube.com/watch?v=XUeu1THIvc0 ) .
NEVER USE Y-VENT WITHOUT TESTING
Pressure support with patient breathing If the patient is breathing,
make sure that the pressure settings are comfortable for him. Settings which are too high may cause discomfort when changing from inhale to exhale.
Weaning seems to be the best way to use the Y-vent if regular ventilators are desperately needed for more difficult cases. The patient should be intubated and the switch from the regular respirator to the Y-vent would be performed after the Y-vent is setup and EEP and EIP are adjusted on a test lung.
Apnea With a passive patient, Y-vent will fall back to a fixed RR. The Y-vent is a very reliable device if 1) the supply pressure is properly set and stable 2) the output loop is sealed off.
MAKE SURE THAT THERE ARE NO LEAKAGES IN THE BREATING LOOP SINCE THIS MAY CAUSE THE VENTILATOR TO STOP. Oxygen titration FURTHER RECOMMENDATIONS WILL FOLLOW

11

## 4.Trouble shooting

### Y-vent not cycling

Possible causes: 1) Unit is not glued properly (internal or external leakages). Fix: Re-assemble 2) The patient loop has leakages, Fix: Seal off leakages/replace the loop, make sure the ETT connector works properly 3) The patient port is blocked. Fix: Remove the blockage.

### Vibrations (the unit is vibrating with high frequency)

Possible causes: 1) Unit is not glued properly (internal or external leakages). Fix: Re-assemble, 2) The patient loop has leakages. Fix: Seal off leakages/replace the loop, make sure the ETT connector works properly 3) The hose in the patient loop is kinked, ETT blocked. Fix: Remove kinks, revise intubation.

### RR too high, need to reduce

Possible causes: 1) Small lungs and or tidal volume. Fix: Use RR adjustment module, or increase the volume of the breathing loop by using longer hose, or reduce supply pressure (warning: it will change EEP and EIP).

### RR too low, need to increase

Fix: Reduce the breathing loop volume. Decrease supply pressure. (warning: it will change EEP and EIP).

12

## 5.Manufacturing and Assembly

- Tools needed - see Attachment B
- Files needed for 3D printing can be obtained at http://3dprintedventilator.com/ OR https://github.com/MSwoboda/Y-Vent (https://github.com/MSwoboda/yvent)

### Explanation

Y-Vent has been designed to be entirely 3D printed. However, CAD and STL file folders include both 3D printable versions and a rough version adapted for CNC milling and injection molding (threads removed, holes sized for tapping, overhangs removed). The design has been printed and tested using Markforged Onyx One and Prusa i3 Mk3 printers.
3D printed versions can be assembled using double sided tape (video: https://www.youtube.com/watch?v=hZ9rezzCuwM) or silicone glue.
Both methods are presented below.

### Medical Grade Silicone Adhesive Method

This method creates a robust seal between the main body and cover using a medical grade silicone rubber. This is the preferred method of sealing the part.

Tools
- Spatula
- Q-Tip
- Medical-grade Silicone Adhesive
- Paper towel
- Glue gun

13

Instructions
1. Remove supports from 3D printed parts and prepare tools.

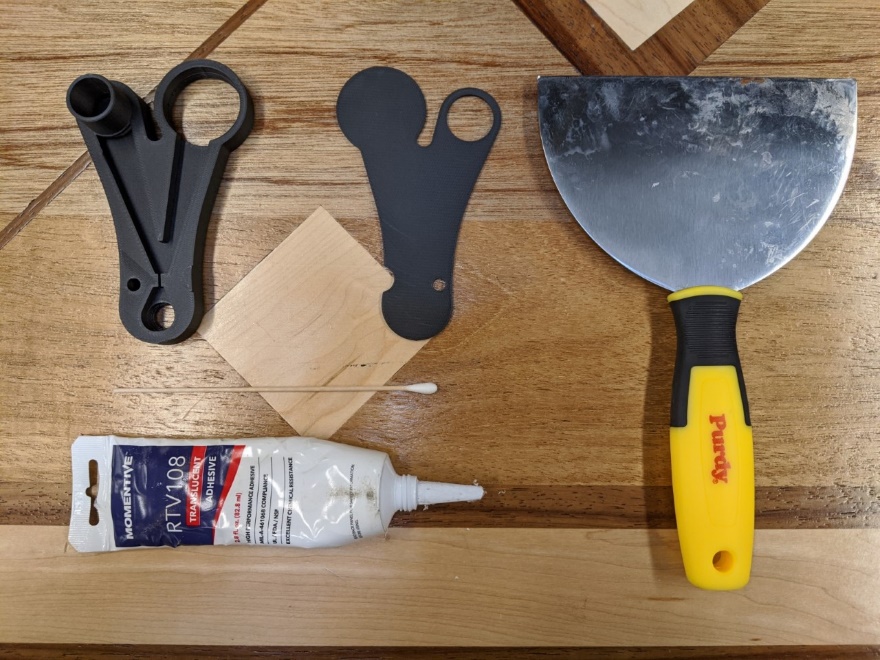
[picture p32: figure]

Figure 4. Tools and parts needed for the first step of Y-vent assembly
Add blob of adhesive to the smooth side of cover (side without writing). The amount of adhesive should be enough to create a thin (0.2-1mm) layer.

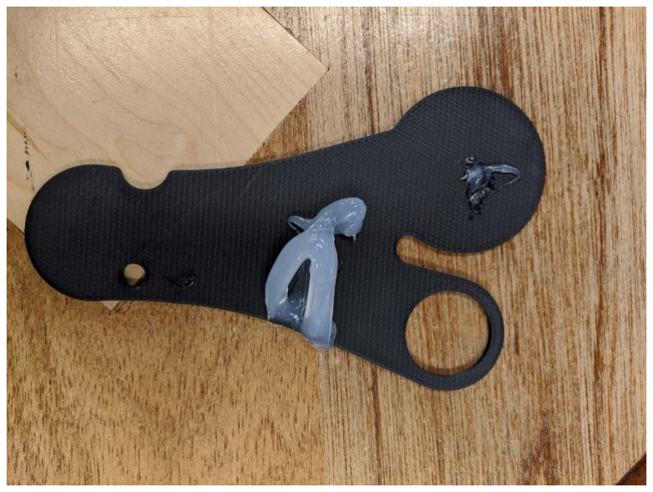
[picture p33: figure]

Figure 5. Glue application

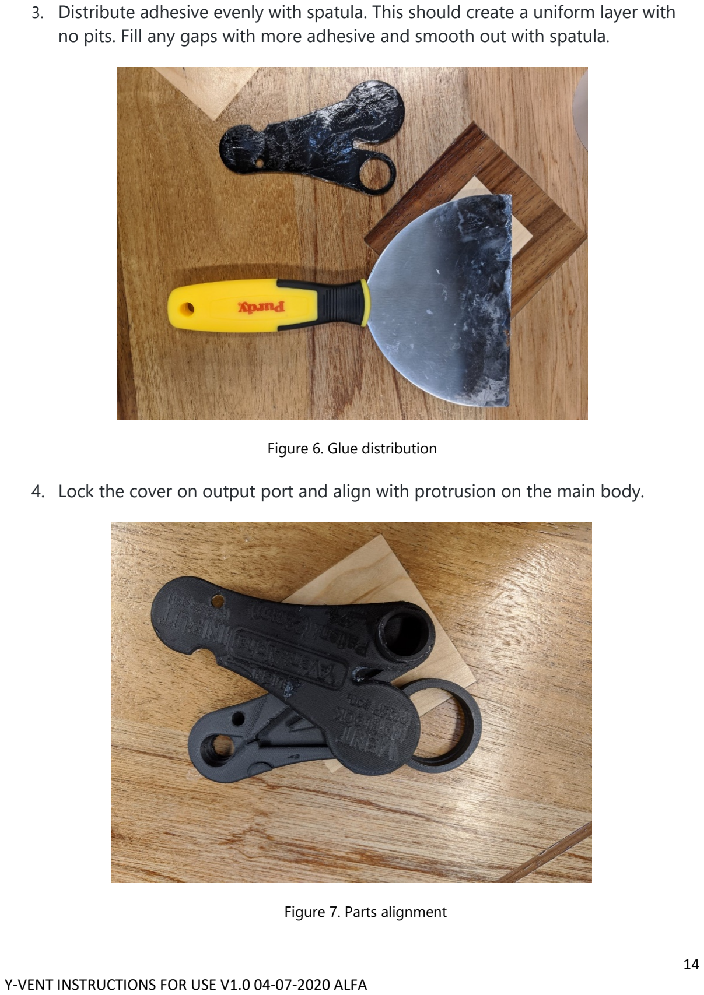
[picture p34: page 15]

14

3. Distribute adhesive evenly with spatula. This should create a uniform layer with no pits. Fill any gaps with more adhesive and smooth out with spatula.

Figure 6. Glue distribution
4. Lock the cover on output port and align with protrusion on the main body.

Figure 7. Parts alignment

15

5. Clean any adhesive leaking out with a paper towel.

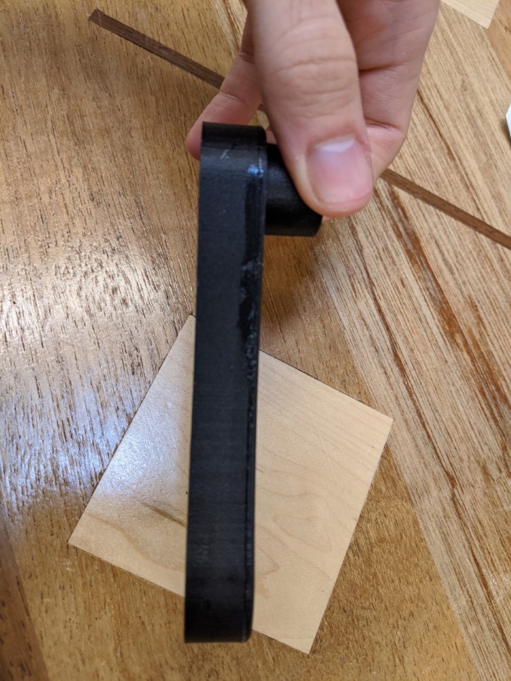
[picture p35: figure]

Figure 8. Excess glue removal
6. Apply pressure to the part and leave to try until adhesive is set. Time and pressure will depend on adhesive type. Note the setting and curing time.

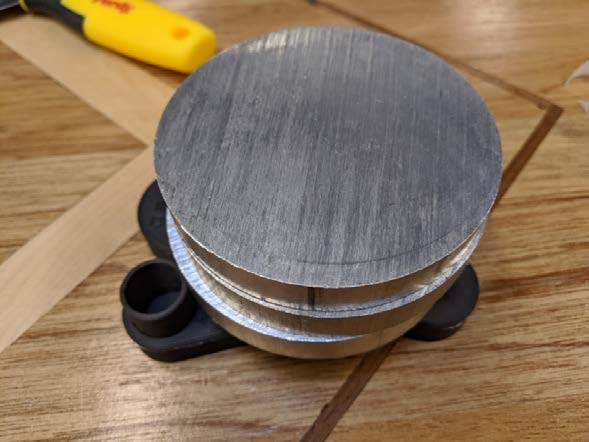
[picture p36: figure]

Figure 9. Cure under pressure

16

### Double Sided Tape Method

(video: https://www.youtube.com/watch?v=hZ9rezzCuwM )

Tools
- Scissors
- Scalpel or sharp knife
- Strong Double-Sided Tape
- Hot air gun (optional)

Instructions
1. Apply a single strip of double-sided tape to cover the input port and one arm of the Y-Vent. A single strip should cover the input port, narrowing at the input port, and wedge dividing the Y-Vent into two channels.

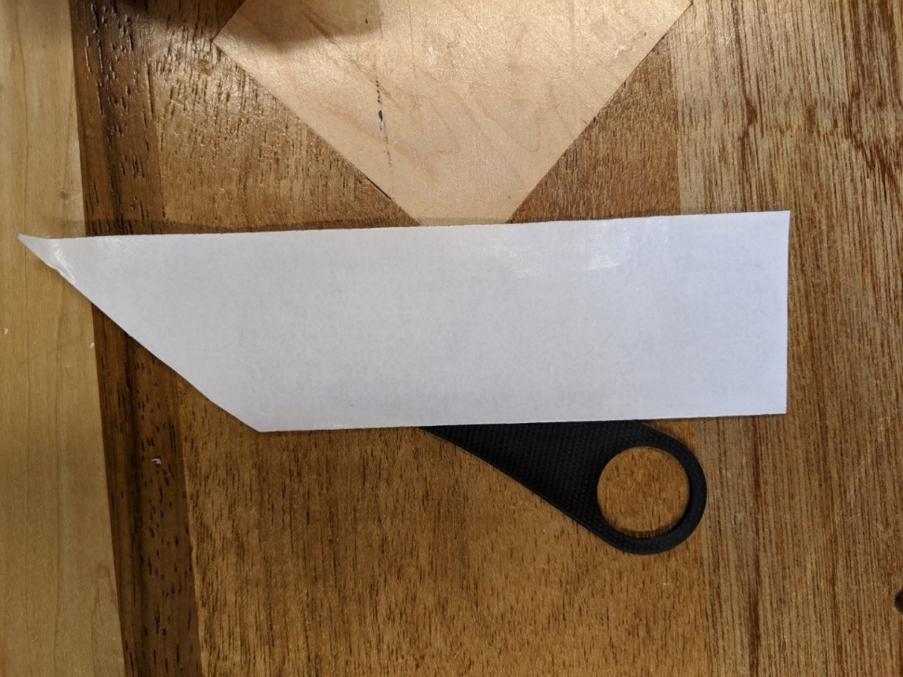
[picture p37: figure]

Figure 10. Double sided tape application, step 1

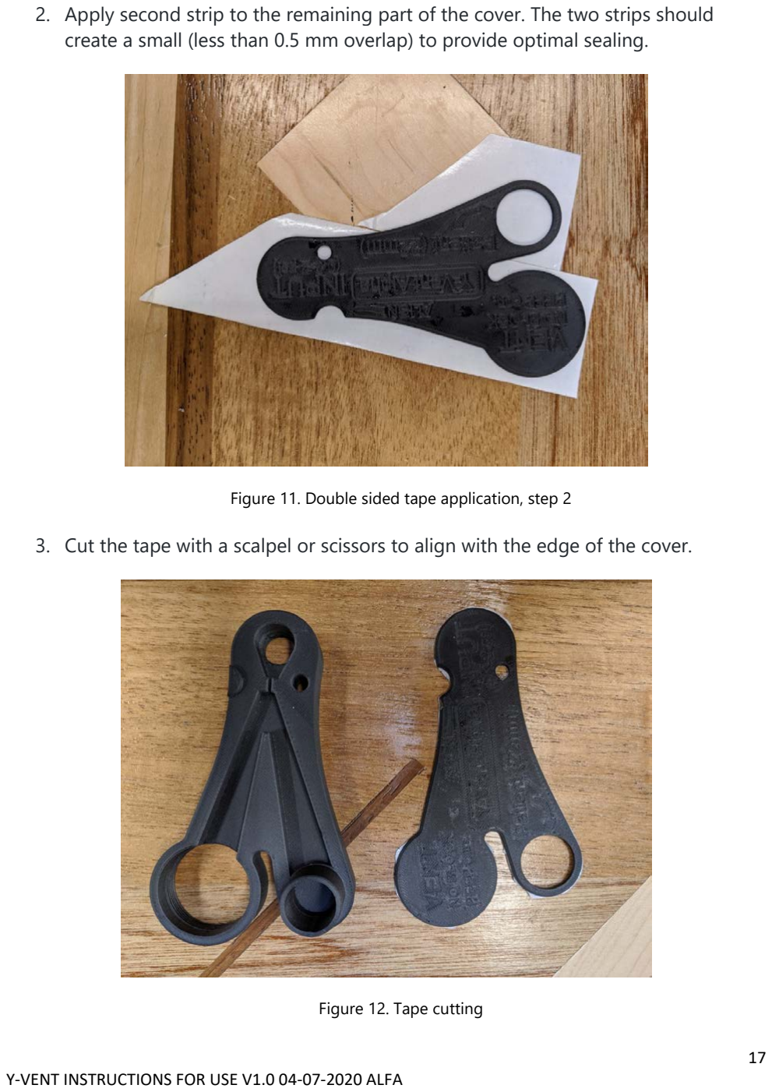
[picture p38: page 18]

17

2. Apply second strip to the remaining part of the cover. The two strips should create a small (less than 0.5 mm overlap) to provide optimal sealing.

Figure 11. Double sided tape application, step 2
3. Cut the tape with a scalpel or scissors to align with the edge of the cover.

Figure 12. Tape cutting

18

4. Lock the cover on the output port and align with protrusion on the main body. Remove any protruding tape with a scalpel. The protruding tape can also be removed with a hot air gun (Note: Apply a small amount of heat to only melt the tape and not the plastic of the Y-Vent).

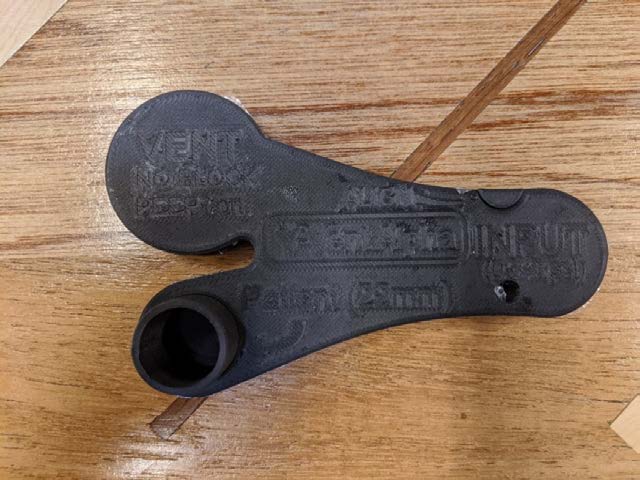
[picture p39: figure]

Figure 13. Parts alignment
5. Apply pressure to the part.

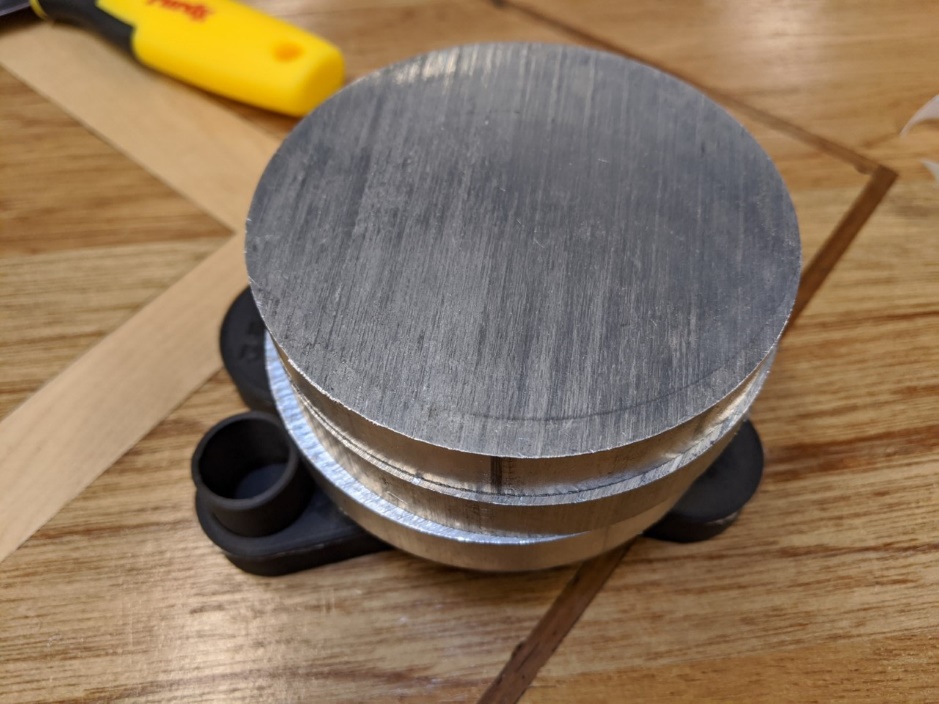
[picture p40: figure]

Figure 14 Cure under pressure

19

Input Port Mount
The Y-Vent has a standard 1/4 NPT thread on the input port, which can fit a wide variety of connectors (like push to connect, barb). Select the connector most appropriate for your environment (testing, clinical). When inserting the connector, apply a small amount of glue to the threads to seal it.
Note: Make sure the connector's edge does not protrude over the floor of the Y-Vent channels.
Note: Make sure that any adhesive applied to the threads does not leak into the input chamber, especially the narrowing after the input port.

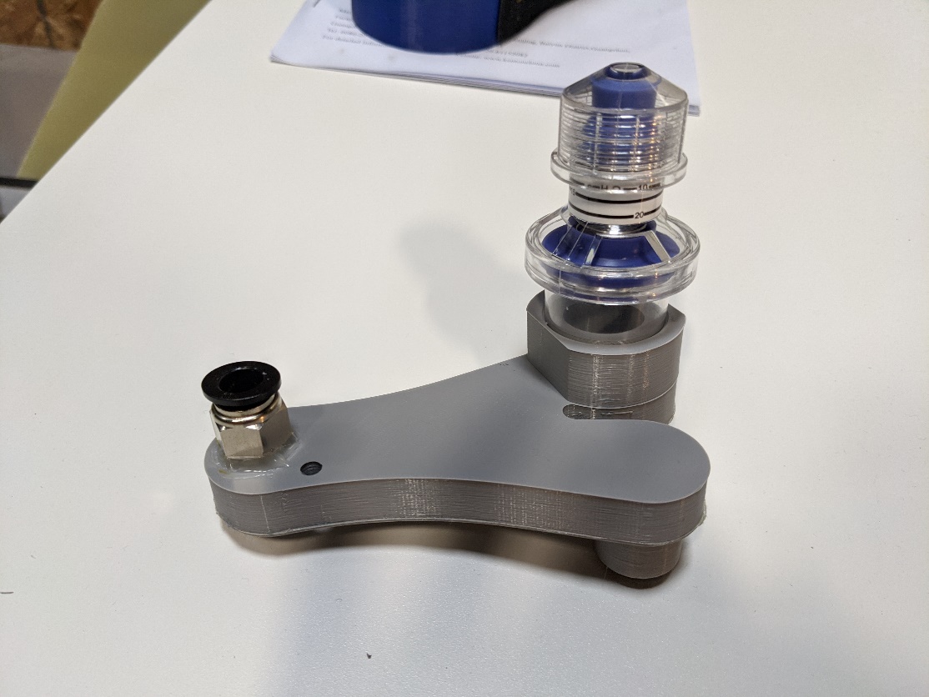
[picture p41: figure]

Figure 15 Fully assembled Y-vent in PEEP configuration

20

## 6. Y-vent verification. Pressure/Flow characteristics

Pressure flow testing
Connect your Y-vent to the pneumatic system as shown in figure 1. Use sensors listed in Attachment B. If pressure sensors are not available, use a makeshift U-tube manometer (video: https://www.youtube.com/watch?v=XUeu1THIvc0).

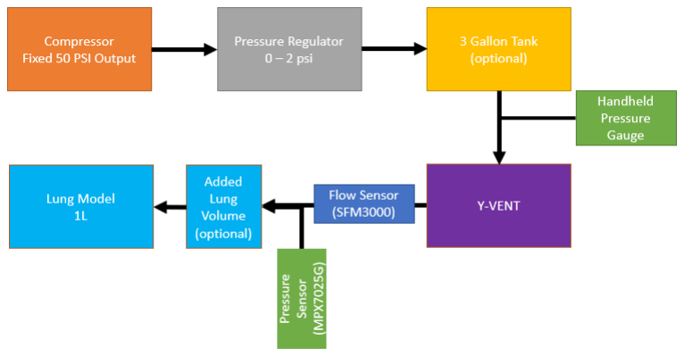
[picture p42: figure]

Figure 16. Flow/Pressure testing setup
Make sure that you pressure source is in agreement with the requirements (see section 2 Supply Pressure).
Testing Procedure ( Y-vent setup: https://www.youtube.com/watch?v=HLaus3BIPC4 )
1. Assemble setup as shown in figure 1 DO NOT CONNECT 50 PSI source to the pressure regulator
2. Check connections for leakages
3. Mount/Adjust PEEP valve to desired level
4. CONNECT 50 PSI source to the pressure regulator
5. Adjust input pressure to desired value (we suggest tests at 40, 60, 80, 100, 120 cmH2O)
6. Measure flow GOTO 5 repeat until 120 cmH2O
7. END

21

Collect Flow pressure data as shown in section 7. Use tables as a guide during operations.

The characteristics printed below are obtained on the ALFA version printed on Markforged ONYX series printer. The unit was working with a patient loop of ~ 1.5 L (with 1 L test lung). The testing setup is the same as shown in Figure 16, but an additional flow sensor is placed before the Y-Vent to measure air flow supply ( F-supply).
Legend: Supply Flow F-Supply, EIP End Inspiratory Pressure, EEP End Expiratory Pressure, F min highest flow during exhale, F max highest flow during inhale, RR Respiratory Rate. Error +/- 2 cmH2O

PEEP configuration characteristics (Pressure/Flow)


Figure 17. Test results

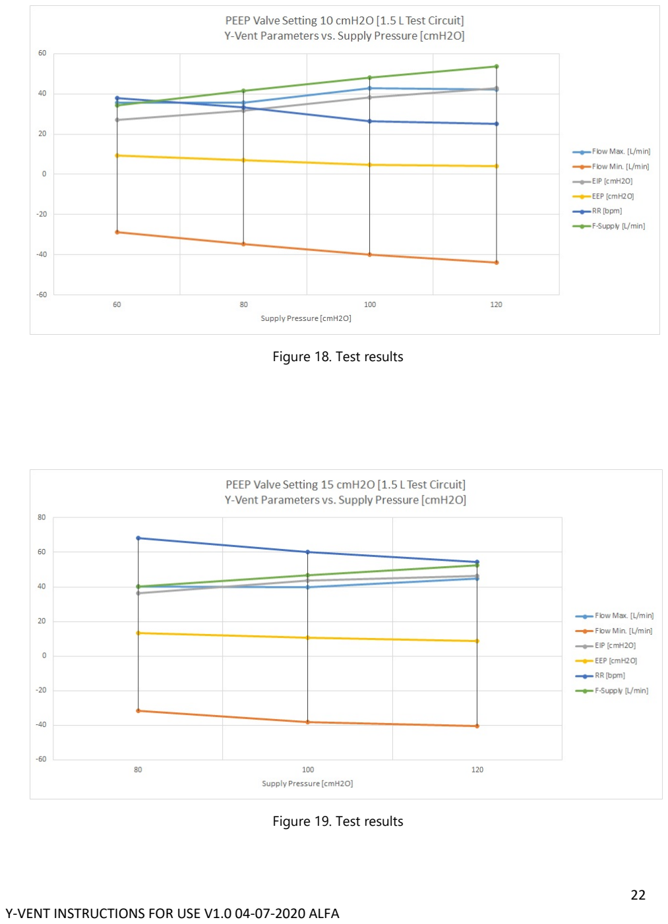
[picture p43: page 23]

22

Figure 18. Test results

Figure 19. Test results

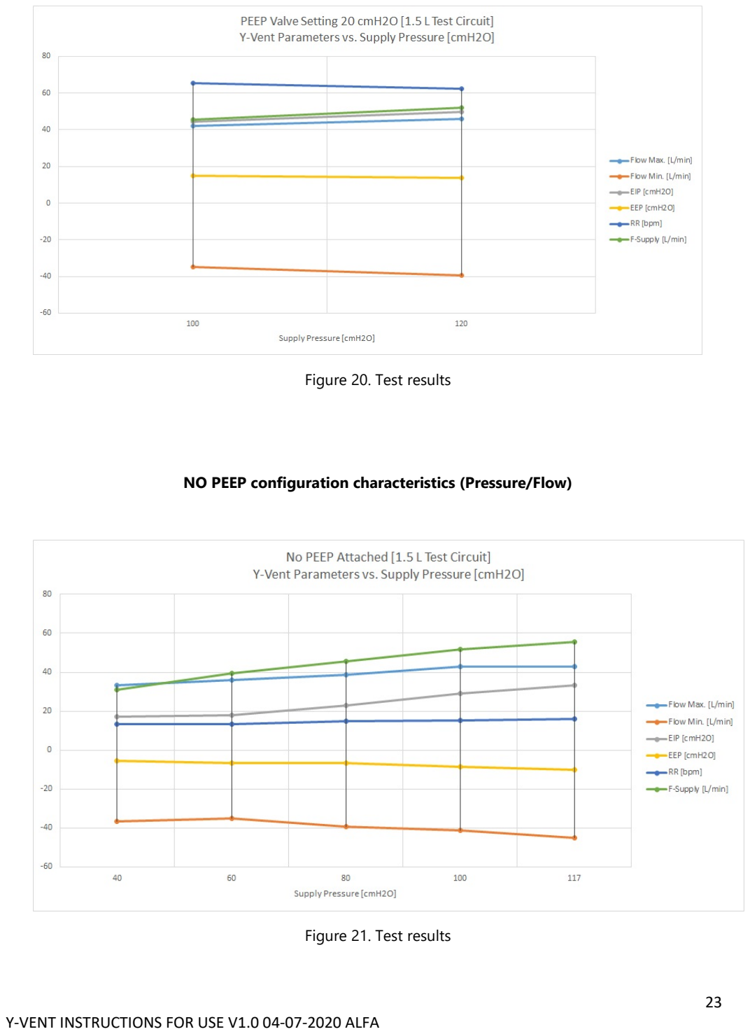
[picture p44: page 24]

23

Figure 20. Test results

NO PEEP configuration characteristics (Pressure/Flow)

Figure 21. Test results

24

Note: PEEP settings do not directly translate to the true PEEP value. Calibrate before use. Most likely PEEP valve settings will need to be greater in order to achieve desired PEEP level.
Y-VENT PRINTED ON DIFFERENT PRINTERS USING DIFFERENT MATERIALS MAY PERFORM DIFFERENTLY
WARNING: ALWAYS CALIBRATE YOUR Y-VENT BEFORE USAGE!

Failure Reporting

We encourage everyone interested in the project to 3D print and try out the Y-Vent on your own. All you need is a 3D printer, lung model (could be a balloon, but ventilator test lungs work best), and a 0.3-2psi pressure source. If you'd like to add PEEP, a PEEP valve is necessary. Please post all problems you encounter in the Github's issues section along with a description of how the device was printed, the test setup, a detailed description of the problem, and possible solutions or send an email to contact@3dprintedventilator.com
http://3dprintedventilator.com/

25

Literature

[1] The Fluid Amplifier and its Application in Medical Devices (https://github.com/MSwoboda/yvent/blob/master/literature/The_Fluid_Amplifier_and_its_Application_in_Medical.pdf)
[2] Taxonomic Trees of Fluidic Oscillators (https://www.epj-conferences.org/articles/epjconf/pdf/2017/12/epjconf_efm2017_02128.pdf)
[3] Experimental Comparison between the Flow Field of Two Common Fluidic Oscillator Designs (https://www.researchgate.net/publication/271645509_Experimental_Comparison_between_the_Flow_Field_of_Two_Common_Fluidic_Oscillator_Designs)

26

Attachment A - List of tested 3D printers

1. Markforged Onyx series
2. Prusa i3 based

27

Attachment B – tools needed

Manufacturing

1. 3D printer
2. Double sided tape (verified brands: Shurtape, www.shurtape.com)
3. X-Acto knife
4. Glue gun (brand tested: Surebonder) the glue gun temperature should be lower than the 3D printer filament melting point. Watch for heat damage during gluing process.
5. For the silicone glue option use RTV 108 adhesive and spatula
6. Q-Tip
7. Paper towel
Verification
1. Pressure transducer with display capabilities. Range: -10 through 200 cmH2O OR
Manometer Range: -10 through 200 cmH2O
OR
Transparent flexible tubing (2.5 m long) filled with water + ruler with centimeter scale Flow meter range -200 through 200 l/min

28

Attachment C
Tested pressure sources:
Air regulators:
- Type 70 Pressure Regulator (Bellofram Corporation)

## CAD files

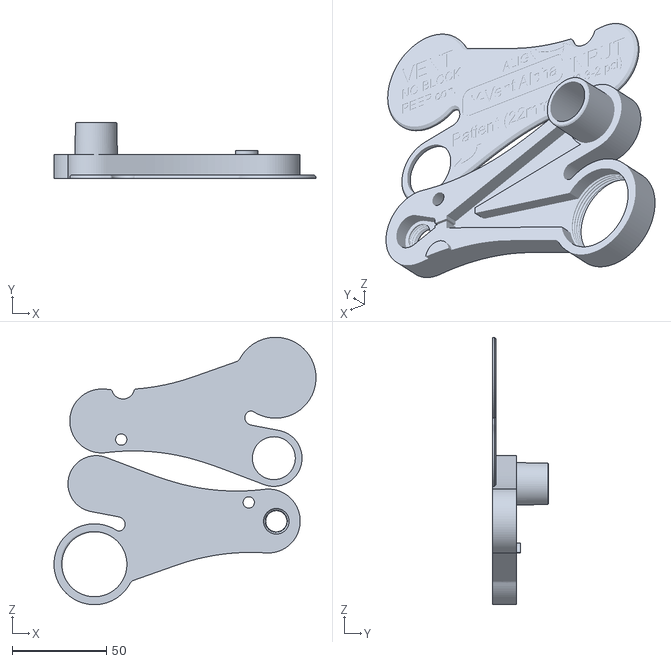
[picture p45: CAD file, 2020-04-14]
CAD files/3D Print/LRV_final_3300_15 v29.stl
139.3 x 30.0 x 142.1

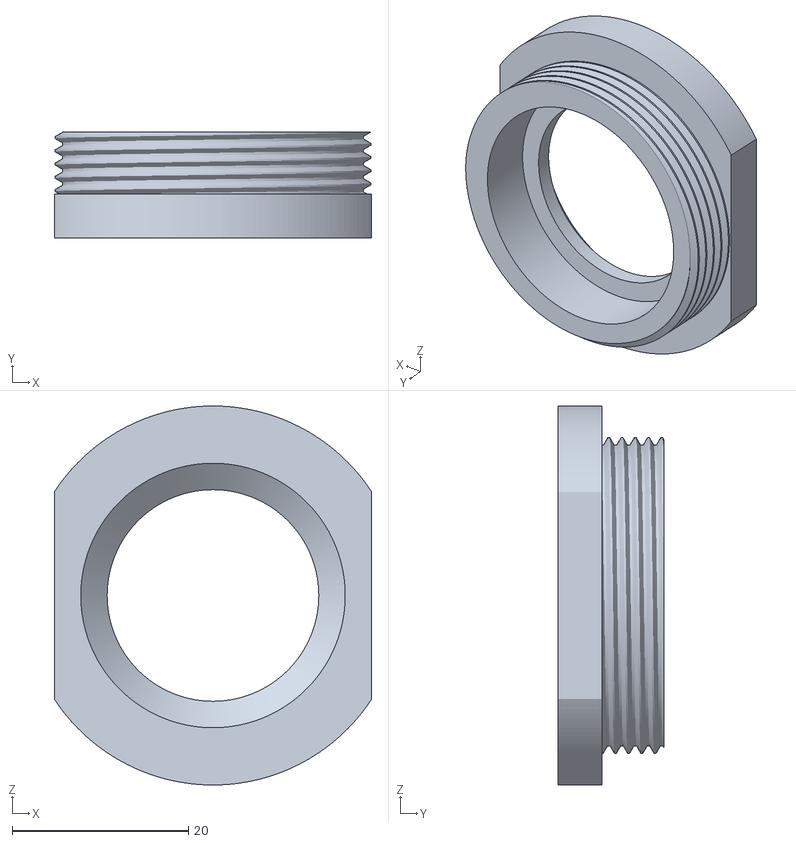
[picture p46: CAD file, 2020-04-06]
STL files/yVentCover_3D_Print.stl
36.0 x 12.0 x 43.0

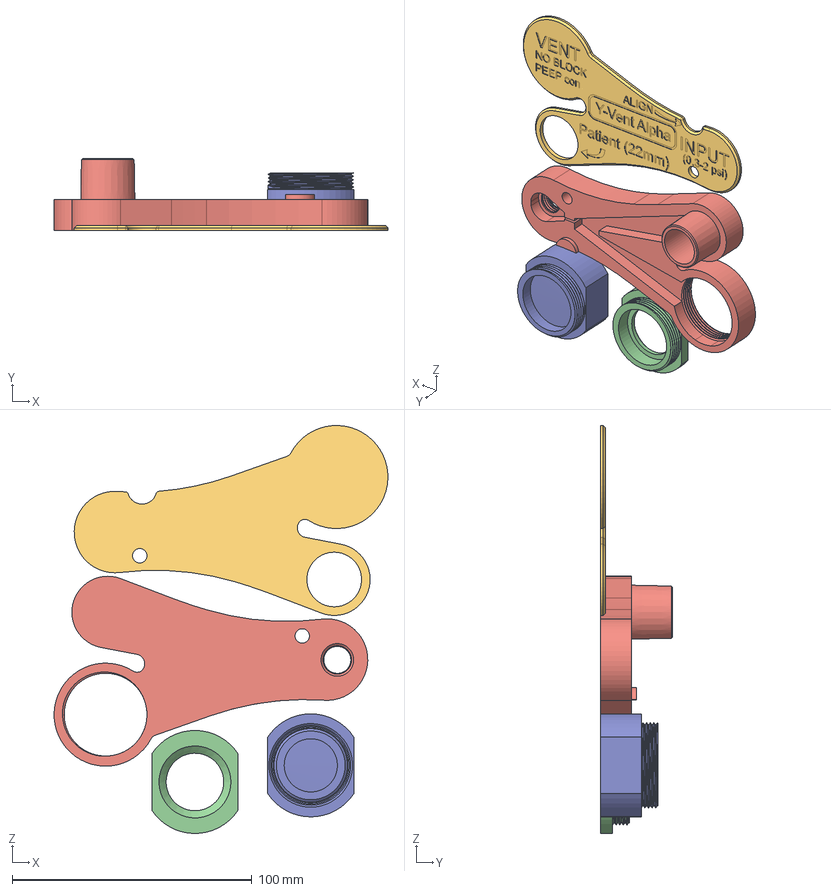
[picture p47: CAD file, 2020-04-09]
CAD files/3D Print/LRV_final_3300_15.step
139.3 x 30.0 x 170.2 mm
yVentTop (1)
yVentBot
Peep Adapter (1)
yVent Cover (1)

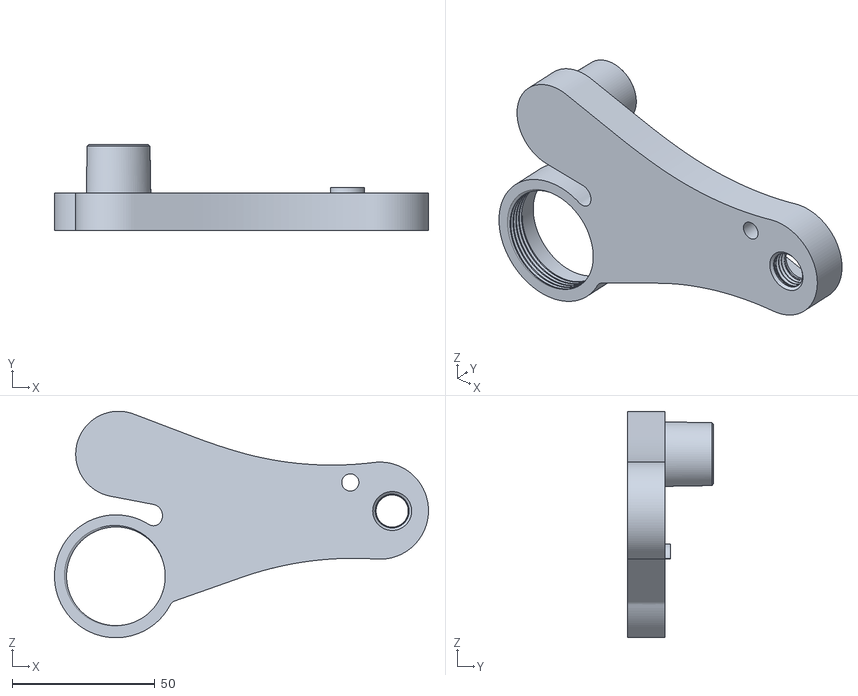
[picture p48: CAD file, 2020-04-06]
STL files/yVentBot_3D_Print.stl
130.9 x 30.0 x 79.3

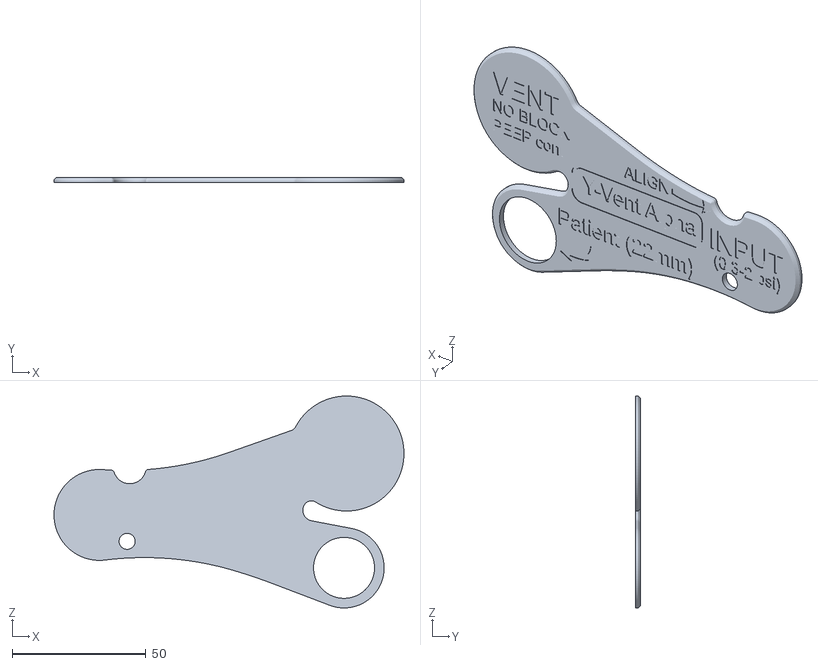
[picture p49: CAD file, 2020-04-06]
STL files/yVentTop_3D_Print.stl
130.9 x 2.06 x 79.2

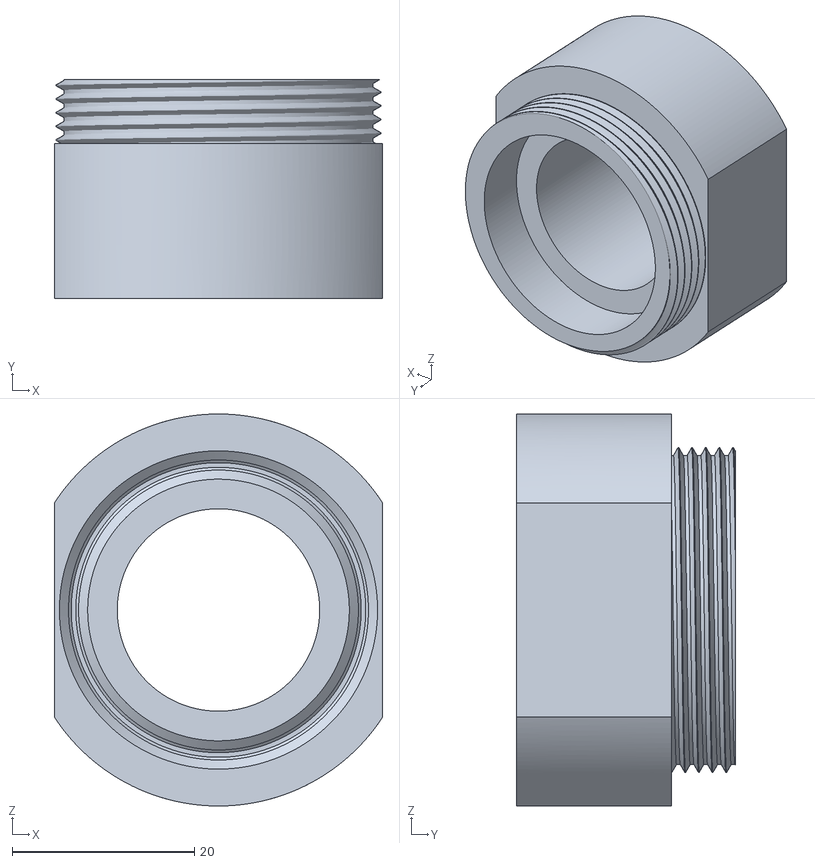
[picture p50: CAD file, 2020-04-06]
STL files/yVentPeep_3D_Print.stl
36.0 x 24.0 x 43.0

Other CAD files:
CAD files/3D Print/yVentBot.f3d
CAD files/3D Print/yVentCover.f3d
CAD files/3D Print/yVentPeepAdapter.f3d
CAD files/3D Print/yVentTop.f3d
CAD files/CNC & Injection Molding Primer/yVentBot_CNC_IM_primer.f3d
CAD files/CNC & Injection Molding Primer/yVentTop_CNC_IM_primer.f3d

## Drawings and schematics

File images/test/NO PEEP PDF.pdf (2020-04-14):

### No PEEP Attached [1.5 L Test Circuit]

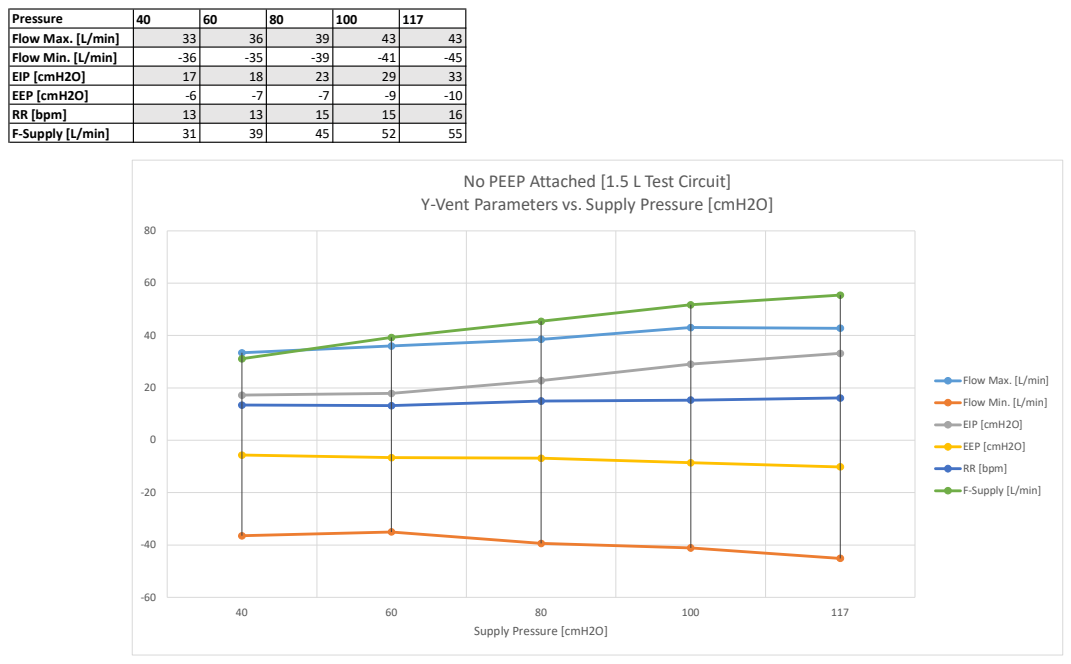
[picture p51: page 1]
Supply Pressure [cmH2O]; Y-Vent Parameters vs. Supply Pressure [cmH2O]; Flow Max. [L/min] Flow Min. [L/min] EIP [cmH2O] EEP [cmH2O] RR [bpm] F-Supply [L/min]

Pressure | 40 | 60 | 80 | 100 | 117
Flow Max. [L/min] | 33 | 36 | 39 | 43 | 43
Flow Min. [L/min] | -36 | -35 | -39 | -41 | -45
EIP [cmH2O] | 17 | 18 | 23 | 29 | 33
EEP [cmH2O] | -6 | -7 | -7 | -9 | -10
RR [bpm] | 13 | 13 | 15 | 15 | 16
F-Supply [L/min] | 31 | 39 | 45 | 52 | 55

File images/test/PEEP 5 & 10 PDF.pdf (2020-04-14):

### PEEP Valve Setting 5 cmH2O [1.5 L Test Circuit]

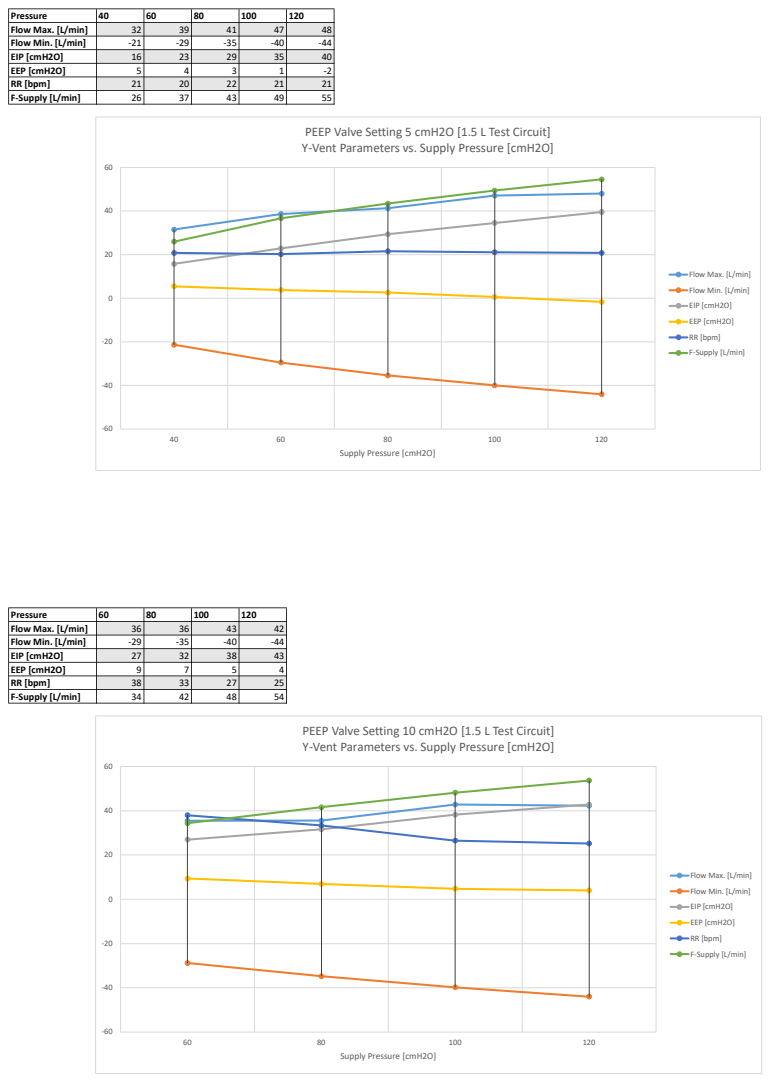
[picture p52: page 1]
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

Pressure | 40 | 60 | 80 | 100 | 120
Flow Max. [L/min] | 32 | 39 | 41 | 47 | 48
Flow Min. [L/min] | -21 | -29 | -35 | -40 | -44
EIP [cmH2O] | 16 | 23 | 29 | 35 | 40
EEP [cmH2O] | 5 | 4 | 3 | 1 | -2
RR [bpm] | 21 | 20 | 22 | 21 | 21
F-Supply [L/min] | 26 | 37 | 43 | 49 | 55

Pressure | 60 | 80 | 100 | 120
Flow Max. [L/min] | 36 | 36 | 43 | 42
Flow Min. [L/min] | -29 | -35 | -40 | -44
EIP [cmH2O] | 27 | 32 | 38 | 43
EEP [cmH2O] | 9 | 7 | 5 | 4
RR [bpm] | 38 | 33 | 27 | 25
F-Supply [L/min] | 34 | 42 | 48 | 54

PEEP Valve Setting 10 cmH2O [1.5 L Test Circuit]

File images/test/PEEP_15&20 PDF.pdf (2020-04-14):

Pressure | 80 | 100 | 120
Flow Max. [L/min] | 40 | 40 | 45

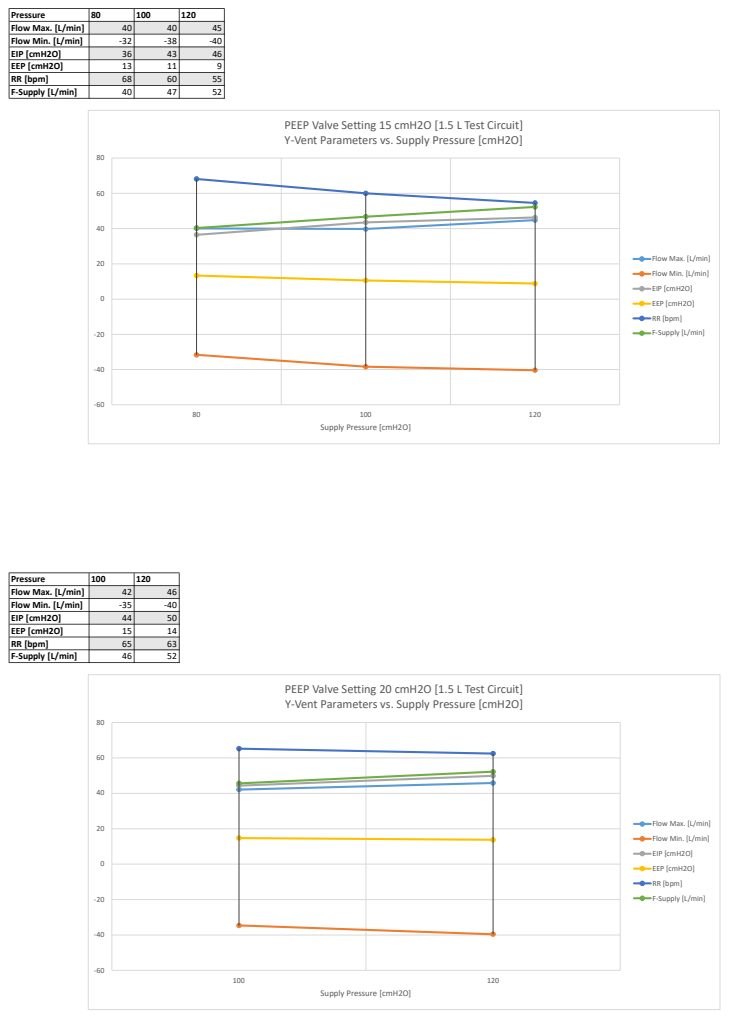
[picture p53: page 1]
Supply Pressure [cmH2O]; Y-Vent Parameters vs. Supply Pressure [cmH2O]; Flow Max. [L/min] Flow Min. [L/min] EIP [cmH2O] EEP [cmH2O] RR [bpm] F-Supply [L/min]; 100 120 Supply Pressure [cmH2O]

Flow Min. [L/min] | -32 | -38 | -40
EIP [cmH2O] | 36 | 43 | 46
EEP [cmH2O] | 13 | 11 | 9
RR [bpm] | 68 | 60 | 55
F-Supply [L/min] | 40 | 47 | 52

PEEP Valve Setting 15 cmH2O [1.5 L Test Circuit]

Pressure | 100 | 120
Flow Max. [L/min] | 42 | 46
Flow Min. [L/min] | -35 | -40
EIP [cmH2O] | 44 | 50
EEP [cmH2O] | 15 | 14
RR [bpm] | 65 | 63
F-Supply [L/min] | 46 | 52

PEEP Valve Setting 20 cmH2O [1.5 L Test Circuit]

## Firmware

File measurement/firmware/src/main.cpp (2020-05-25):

#define MEGUNO_LINK
// #define SERIAL_LINK

#include <Arduino.h>
#include "SFM3000wedo.h"
#include <Wire.h>

SFM3000wedo measflow(64);

int offset = 32000;  // Offset for the sensor
float scale = 140.0; // Scale factor for Air and N2 is 140.0, O2 is 142.8

float pressureVoltage = 0;
float Pressure = 0;
float pressureOffset = 0;
float Flow = 0;

unsigned int result = 0;

const unsigned SendInterval = 20; // [ms]

#ifdef MEGUNO_LINK
#include "MegunoLink.h" // Helpful functions for communicating with MegunoLink.

// Millis value when the data was last sent.
long LastSent;

// Interval (milliseconds) between sending analog data

// The plot we are sending data to.
TimePlot FlowPlot;
TimePlot PressurePlot;

#endif

void setup()
{
  Wire.begin();
  Serial.begin(9600);
  delay(500);

  pinMode(A0, INPUT);
  measflow.init();

  pressureVoltage = (5.000 / 1023.000) * analogRead(A0);
  pressureOffset = -1.000 * (pressureVoltage - 2.50) / 0.09;

#ifdef MEGUNO_LINK

  LastSent = millis();

  FlowPlot.SetTitle("Flow Measurement");
  FlowPlot.SetXlabel("Time");
  FlowPlot.SetYlabel("Value");
  FlowPlot.SetSeriesProperties("Flow", Plot::Red, Plot::Solid, 2, Plot::Square);

  PressurePlot.SetTitle("Pressure Measurement");
  PressurePlot.SetXlabel("Time");
  PressurePlot.SetYlabel("Pressure");
  PressurePlot.SetSeriesProperties("Pressure", Plot::Blue, Plot::Solid, 2, Plot::Square);
  
#endif
}

void loop()
{

  if ((millis() - LastSent) > SendInterval)
  {
    LastSent = millis();

    result = measflow.getvalue();

    Flow = ((float)result - offset) / scale;

    pressureVoltage = (5.000 / 1023.000) * analogRead(A0);
    Pressure = 10.1972*((pressureVoltage - 2.5) / 0.09) + pressureOffset;

#ifdef SERIAL_LINK

    Serial.print(Flow, 2);
    Serial.print(",");
    Serial.print(Pressure );
    Serial.print("\n");
#endif
#ifdef MEGUNO_LINK

    FlowPlot.SendData("Flow", Flow);
    PressurePlot.SendData("Pressure", Pressure);

#endif
  }
}

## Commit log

2020-03-27 data added
    [data_adjustable_prototype_15cmh2o_03272020.csv, distance_table.xlsx]
2020-03-30 data1 added
    [100cmh2o.csv, 110cmh2o.csv, 120cmh2o.csv, 130cmh2o.csv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]
2020-03-30 added second version tests
    [yventv2_100cmH2O.csv, yventv2_30_last5cycles_35_cmH2O.csv, yventv2_40cmH2O.csv, yventv2_50cmH2O.csv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]
2020-04-03 added peep test data
    [yvent_v3_120cmH2O.csv, yvent_v3_150cmH2O.csv, yvent_v3_40cmH2O.csv, yvent_v3_80cmH2O.csv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]
2020-04-03 added folders
    [100cmh2o.csv, 110cmh2o.csv, 120cmh2o.csv, 130cmh2o.csv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]
2020-04-03 moved data
    [100cmh2o.csv, 110cmh2o.csv, 120cmh2o.csv, 130cmh2o.csv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]
2020-04-05 added flow station firmware
2020-04-06 assembly pics added
    [yVentBot_3D_Print.stl, yVentCover_3D_Print.stl, yVentPeep_3D_Print.stl, yVentTop_3D_Print.stl]
2020-04-09 cad files added
    [LRV_final_3300_15.step, yVentBot.f3d, yVentBot_CNC_IM_primer.f3d, yVentCover.f3d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]
2020-04-14 added IFU fov
    [LRV_final_3300_15 v29.stl]
